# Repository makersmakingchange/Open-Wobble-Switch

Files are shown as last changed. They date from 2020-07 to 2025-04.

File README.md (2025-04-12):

# Open Wobble Switch

## Overview
The Open Wobble Switch is a cost effective, open source assistive switch similar to commercially available Wobble Switches. The switch is activated by applying force to and moving a wand in any direction. The switch can be activated by various body parts including the limbs and head. It provides a momentary closed contact that can be used to activate various assistive devices. The Open Wobble Switch has an interchangeable topper that can be swapped for different shapes and sizes. The switch requires approximately 0.55 N (55 gf) and about 24 mm of travel to operate, though this will vary a bit depending on the topper attached. 

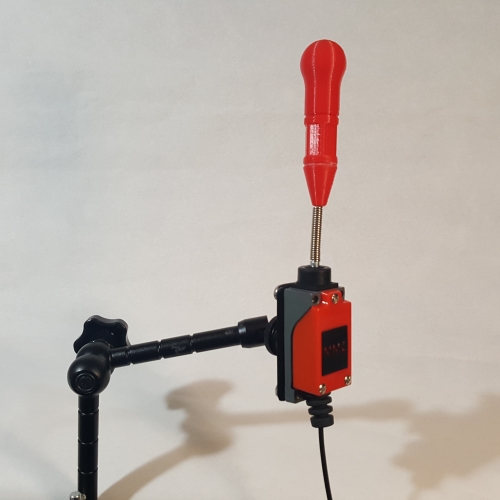
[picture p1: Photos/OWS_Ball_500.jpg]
Open Wobble Switch


Last Updated: 2024-Mar-21

## More info at
- [Makers Making Change Device Page](https://www.makersmakingchange.com/project/open-wobble-switch/)

## Getting Started

### 1. Order the Off-The-Shelf Components

The [Bill of Materials](/Documentation/Open_Wobble_Switch_BOM.xlsx) lists all of the parts and components required to build the Open Wobble Switch. The main switch component needs to be ordered online. The rest of the off-the-shelf components are also online or may be available in smaller quantities at your local hardware store or dollar store.

### 2. Print the 3D Printable components

Print the components for the switch and one or more toppers.

All of the files and individual print files can be in the [/Build_Files/3D_Printing_Files](/Build_Files/3D_Printing/) folder.

### 3. Assemble the Switch and Toppers

Reference the [assembly instructions](/Documentation/Open_Wobble_Switch_Instructions.pdf) for the tools and steps required to build each portion.

## Files
### Documentation
| Document             | Version | Link |
|----------------------|---------|------|
| Design Rationale     | 1.1     | [Open_Wobble_Switch_Design_Rationale](/Documentation/Open_Wobble_Switch_Design_Rationale.pdf)     |
| Bill of Materials    | 1.1     | [Open_Wobble_Switch_BOM](/Documentation/Open_Wobble_Switch_BOM.csv)     |
| Assembly Guide       | 1.1     | [Open_Wobble_Switch_Instructions](/Documentation/Open_Wobble_Switch_Instructions.pdf)     |
| Maker Checklist      | 1.1     | [Open_Wobble_Switch_Checklist](/Documentation/Open_Wobble_Switch_Checklist.pdf)     |
| Quick Guide          | 1.1     | [Open_Wobble_Switch_Quick_Guide](/Documentation/Open_Wobble_Switch_Quick_Guide.pdf)    |
| Changelog            | 1.1     | [Open_Wobble_Switch_Changelog](/Documentation/Open_Wobble_Switch_Changelog.pdf)     |

### Design Files
[CAD Files](/Design_Files)

### Build Files
 - [3D Printing Files](/Build_Files/3D_Printing)
 - [V1.1 3MF](/Build_Files/3D_Printing/OWS_All_v1.1.3mf)

## Attribution
Designers:
 - Birk Zukowsky
 - Gabriel Chu
 - Jake McIvor

## License
<br /><span xmlns:dct="http://purl.org/dc/terms/" property="dct:title">Open Wobble Switch</span> by <a xmlns:cc="http://creativecommons.org/ns#" href="www.makersmakingchange.com" property="cc:attributionName" rel="cc:attributionURL">Neil Squire</a> is licensed under a <a rel="license" href="http://creativecommons.org/licenses/by-sa/4.0/">Creative Commons Attribution-ShareAlike 4.0 International License</a>.

---
<!-- ABOUT MMC START -->
## About Makers Making Change
[Makers Making Change Logo](https://www.makersmakingchange.com/)

Makers Making Change is a program of [Neil Squire](https://www.neilsquire.ca/), a Canadian non-profit that uses technology, knowledge, and passion to empower people with disabilities.

Makers Making Change leverages the capacity of community based Makers, Disability Professionals and Volunteers to develop and deliver affordable Open Source Assistive Technologies.

 - Website: [www.MakersMakingChange.com](https://www.makersmakingchange.com/)
 - GitHub: [makersmakingchange](https://github.com/makersmakingchange)
 - Bluesky: [@makersmakingchange.bsky.social](https://bsky.app/profile/makersmakingchange.bsky.social)
 - Instagram: [@makersmakingchange](https://www.instagram.com/makersmakingchange)
 - Facebook: [makersmakechange](https://www.facebook.com/makersmakechange)
 - LinkedIn: [Neil Squire Society](https://www.linkedin.com/company/neil-squire-society/)
 - Thingiverse: [makersmakingchange](https://www.thingiverse.com/makersmakingchange/about)
 - Printables: [MakersMakingChange](https://www.printables.com/@MakersMakingChange)

### Contact Us
For technical questions, to get involved, or to share your experience we encourage you to [visit our website](https://www.makersmakingchange.com/) or [contact us](https://www.makersmakingchange.com/s/contact).
<!-- ABOUT MMC END -->

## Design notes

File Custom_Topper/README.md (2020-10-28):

# Custom Toppers for the Open Wobble Switch

One of the unique features of the Open Wobble Switch is the ability to swap the toppers and create custom toppers. To make the process of creating a custom topper as easy as possible, we've included some additional files and instructions.

The switch has an M12-1.75 x 7mm length external thread to interface with the topper.

## OpenSCAD
https://dkprojects.net/openscad-threads/

## TinkerCAD
https://www.tinkercad.com/things/hLjlR0M9PSN-openwobbletopper-flat

## Fusion 360

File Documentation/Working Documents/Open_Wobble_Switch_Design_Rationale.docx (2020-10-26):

# Introduction

A wobble switch is an assistive switch that can be activated by moving a wand topper. Wobble switches are useful for a variety of users, but can be especially useful for those with poor gross motor control. These switches can be mounted easily and activated by pushing the wand in any direction. The switches can be operated with very little force. The switches can be activated with various parts of the body including: hands, head, chin, tongue through cheek.

Activating the wobble switch completes the circuit and activates the other end. When the 3.5 mm plug is inserted into an input, it activates the device it is plugged into. The switch can be plugged into different devices such as the Xbox Adaptive Controller to act as an extension of a button. This enables the user to activate a multitude of devices (or device buttons) without the use of fine motor control.

Commercial Options

Table 1 Commercially Available Wobble Switches

Name | Vendor | Cost | Link
Ultimate Assistive Technology Switch | Enabling Devices | $80 USD Switch, $150 USD w/ mount | https://enablingdevices.com/product/ultimate-switch/
Wobble Switch | Prentrom | $195 | https://store.prentrom.com/wobble-switch
Wobble Switch | AbleNet | $100 USD | https://www.ablenetinc.com/wobble-switch
Wobble Switch | AMDi | $100 USD | https://www.amdi.net/products/switches/wobble-switch/

# Switch Selection

The existing commercial switches appeared to be a modified commercial product, so this provided a starting point for the design. A similar looking industrial switch was found and tested and provided similar functionality.

## Mini Limit Switch

The switch selected for the base of the Wobble Switch is a ME-8169, which is available from a number of different manufacturers. This limit switch is typically used for CNC machines and there are a few different variants for the activation end. The end most suitable for a Wobble switch is the ‘Flexible Spring Arm’.

An alternative design may be the ME-9101. This variant is typically listed as a ‘flexible spring arm limit switch’. Instead of the wire, it features a longer coil. (https://www.amazon.ca/Uxcell-Me-9101-Momentary-Adjustable-Flexible/dp/B00UBWK8X6)

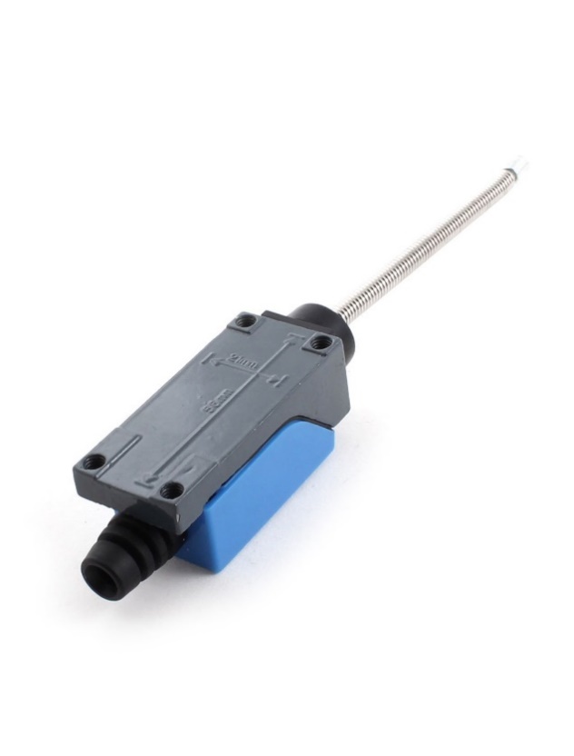
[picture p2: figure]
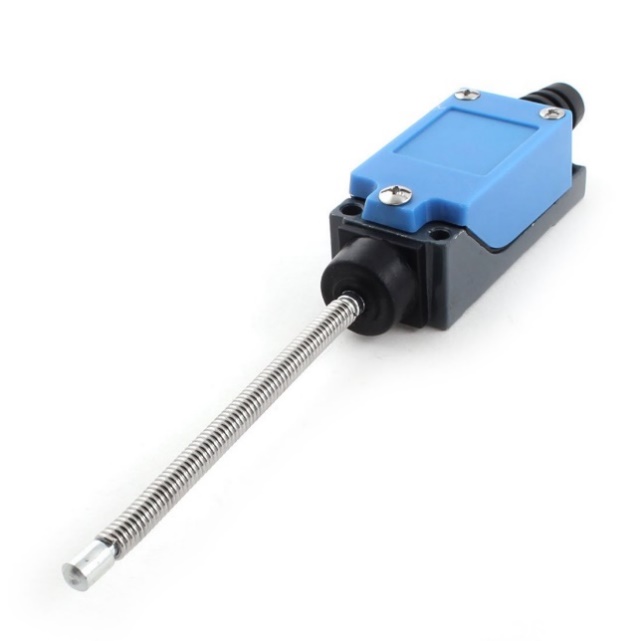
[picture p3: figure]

# Mounting

To keep the switch versatile, it must be easy to mount in a variety of positions and easy to fine-tune the adjustment. Like many of the open source assistive technology, we chose to include a female ½-20 UNC thread so that the switch could be mounted using camera and tripod accessories as well as most other standard assistive technology mounting solutions.

The limit switch has four threaded holes in the metal base spaced on a rectangle 21 mm x 56 mm. This bolt pattern appears to be consistent between manufacturers and different limit switch styles.

The mounting adapter was designed to utilize a ¼-20 UNC, 5/16" tee nut and the four existing mounting holes in the switch. It attaches using 4 M5x0.8 by 10 mm long machine screws. Pan head machine screws, ideally with a Phillips drive, were selected to provide a low profile and so a common screwdriver could be used instead of a hex key.

## Mounting options

- Gooseneck
- Articulating arm / Magic arm (e.g. https://www.amazon.ca/SmallRig-Adjustable-Articulating-Monitor-Lights-2066/dp/B076KDDBW5, $20)
- Loc-Line

# Wand Topper

The bare wire of the limit switch has a pointy end and is not safe to be used on its own. Commercial wobble switches tend to have a ball or rounded cylinder that cover the activation portion.

The initial design for the wire topper was a 4 part design, but this was too challenging to assemble.

Feedback was received on the initial proof of concept prototype that a Tee-shaped topper / handle would be useful.

A versatile feature of the wobble switch is its adaptable toppers. An anchored hex-grip base with extended threads allows for the customizability of different toppers. The T-Topper consists of five separate pieces: the socket, the top and bottom halves of the T, and two pins to hold the halves in the correct position when assembling. The socket was created to allow the female threads to be printed upwards (yielding more accurate 3D printed threads), while enabling the two T halves to be printed on the flat surface to avoid the use of support material. The same theory applies to the Ball-Topper, which only uses one pin. Printing the file vertically is the most logical orientation for the Hand-Topper, which is why the socket is combined into one file and printed as one piece.

Other attachment methods were ideated for attaching both the wand to the wire as well as between the base and the topper. Different methods were sketched, and some were prototyped such as dove tails and varying threads. Super glue was discovered to be the best option in connecting the base to the wire as the burr on the end on most units’ wire, along with inconsistent 3D printer tuning and accuracy, could not be proven to work consistently without high dexterity.

There is potential for future topper designs to be created. Depending on what is requested by an Occupational Therapist or user of the wobble switch, different toppers can be built to suit their needs, for either functionality, aesthetics, or personal interests. Figure 3 shows a variety of possible topper options.

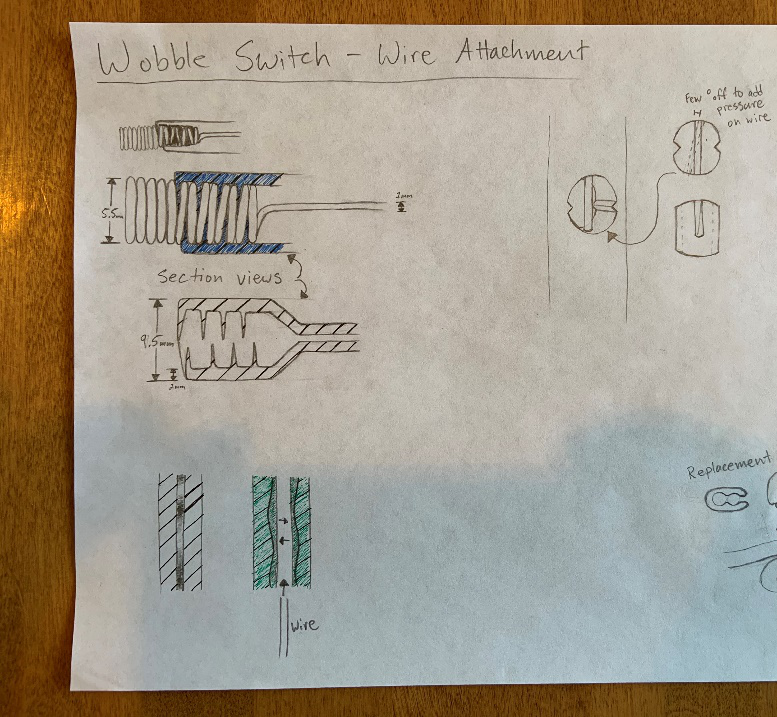
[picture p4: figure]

Figure 1: Wire Attachment Ideation

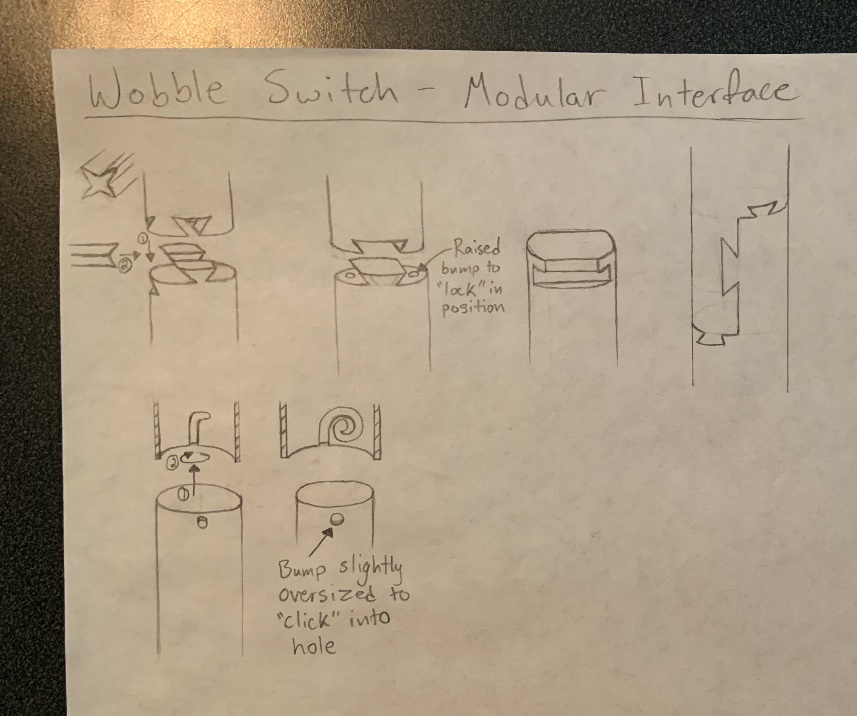
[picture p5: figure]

Figure 2: Modular Interface Ideation

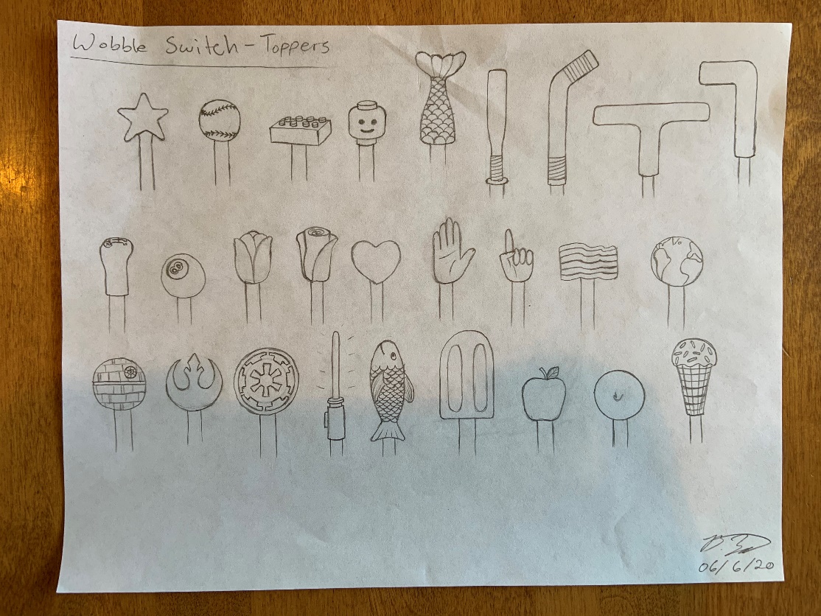
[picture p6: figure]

Figure 3: Wobble Switch Topper Ideation

# Testing

A preliminary proof of concept was tested with several users in an adaptive gaming setup. The wobble switch was mounted to an articulated arm and positioned near the face to provide an additional input to the Xbox Adaptive Controller.

# Version 1.1 Changes

This section will cover the changes and updates that was discussed in the previous section. The design changes focus more on improving the earlier design.

# Toppers

The original toppers were designed with a topper socket in the design which resulted in the need to print the topper pieces in half to properly mount and assemble. Example below.

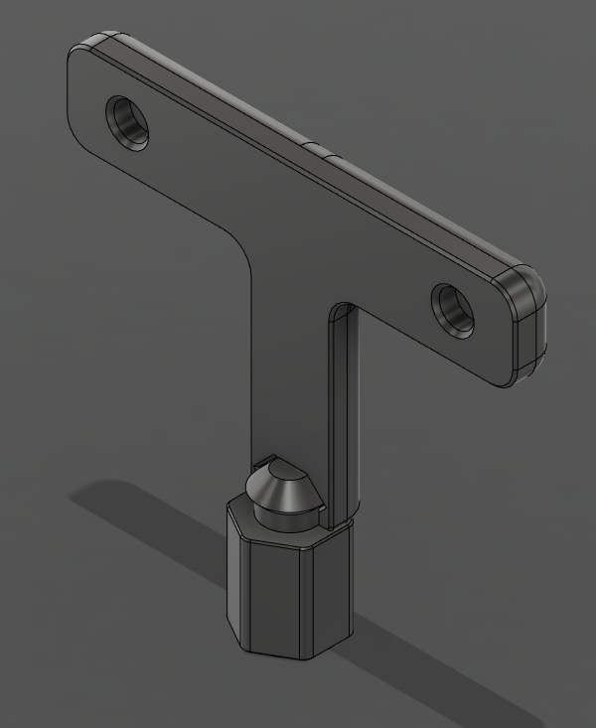
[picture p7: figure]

This made the assembly a little bit more complicated and required the use of glue between the two halves of the topper which, depending on the user, may not have enough glue to secure the two halves together. One idea to solve this process was to integrate a thread into the base of the topper and to print the topper as one piece. Shown below.

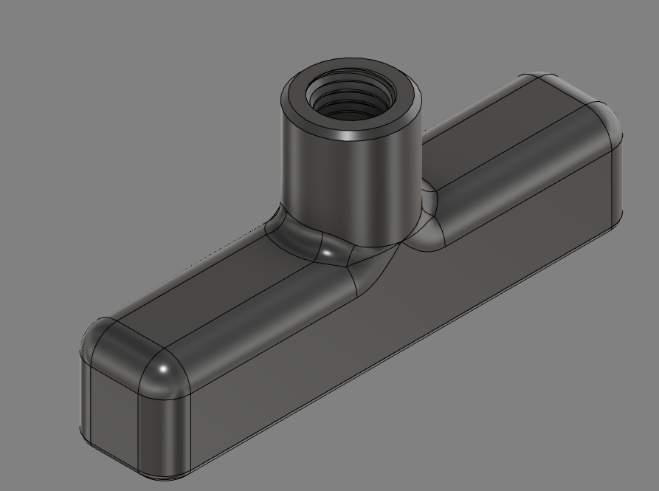
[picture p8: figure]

With the integrated thread we can make the topper piece shorter as well as take away the topper socket piece. This solves another issue with the original design where the weight of the topper assembly causes the switch to bend and possibly activate due to the weight of the assembly. The same concept is used for the other toppers that were designed for example, a rounded ball topper. The topper socket in the original design allows the topper piece to rotate which is undesirable but will be discussed in the next section.

# Topper Socket

The topper socket that was originally designed allows for the assembly and mounting of the topper pieces. However, with the switch having the ability to rotate, the topper socket’s original design with its own ability to rotate the top piece is no desired. Therefore, the topper socket was changed from a circular socket to a squarer or hexagonal shape to limit the amount of rotation of the topper piece. The main function of the topper socket is to allow custom pieces designed by users to be mounted onto the wobble switch.

# Male Threaded Piece

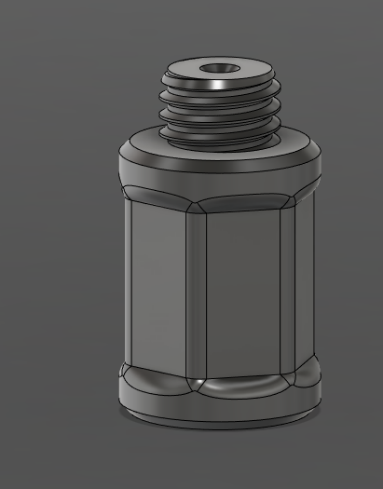
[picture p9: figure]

The male threaded piece shown above is the main mounting piece of the wobble switch assembly. One issue that arose when threading on the topper socket and this piece is that the hexagonal shapes may not match up and would have a sharp corner when the two pieces are threaded together. So, the top was rounded to take away the shape edge and any misalignment issues. This rounding is also done to the bottom of the piece so that it can also transition to the bottom piece.

# Bottom Transition Piece

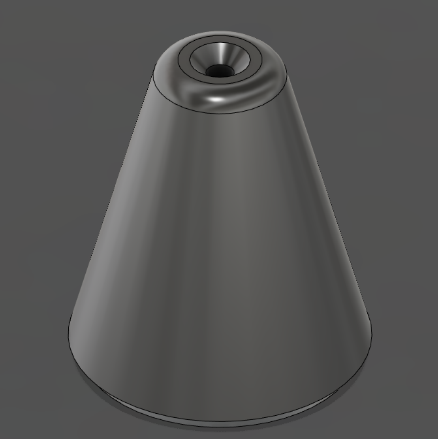
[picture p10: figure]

This transition piece is based off of the original Gluing jig and is mainly used as both a smoothing transition piece as well as the gluing jig for the entire assembly. This smoothens the transition between the wire and the handle pieces.

© 2020 by Neil Squire. “Open Wobble Switch Design Rationale” is licensed under the CC BY SA 4.0 License: http://creativecommons.org/licenses/by-sa/4.0 PAGE 1 OF 3 Design files available at https://www.makersmakingchange.com/project/open-wobble-switch/

V1.1 | OCTOBER 2020 Open Wobble Switch design rationale

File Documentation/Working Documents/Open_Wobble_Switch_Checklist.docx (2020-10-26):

To-do

- Determine which topper(s) the user wants
- Acquire off-the-shelf components
- Print 3D printable components
- Assemble the switch
- Test the switch
- Clean and disinfect the switch
- Package the switch in a sealed bag
- Print the Quick Guide

Items to Deliver to User

- Assembled, Tested, and cleaned Switch
- Quick Guide

© 2020 by Neil Squire. “Open Wobble Switch Maker Checklist” is licensed under the CC BY SA 4.0 License: http://creativecommons.org/licenses/by-sa/4.0 PAGE 1 OF 3 Design files available at https://www.makersmakingchange.com/project/open-wobble-switch/

V1.1 | OCTOBER 2020 Open Wobble Switch MAKER CHECKLIST

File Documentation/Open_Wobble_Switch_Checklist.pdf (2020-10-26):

V1.1 | OCTOBER 2020

# Open Wobble Switch

MAKER CHECKLIST

© 2020 by Neil Squire. (https://neilsquire.ca/) “Open Wobble Switch Maker Checklist” is licensed under the CC BY SA 4.0 License: http://creativecommons.org/licenses/bysa/4.0 (http://creativecommons.org/licenses/by-sa/4.0)
Design files available at https://www.makersmakingchange.com/project/open-wobble-switch/ | PAGE 1 OF 1

To-do

ð Determine which topper(s) the user wants
ð Acquire off-the-shelf components ð Print 3D printable components
ð Assemble the switch
ð Test the switch
ð Clean and disinfect the switch
ð Package the switch in a sealed bag ð Print the Quick Guide

Items to Deliver to User

ð Assembled, Tested, and cleaned Switch
ð Quick Guide

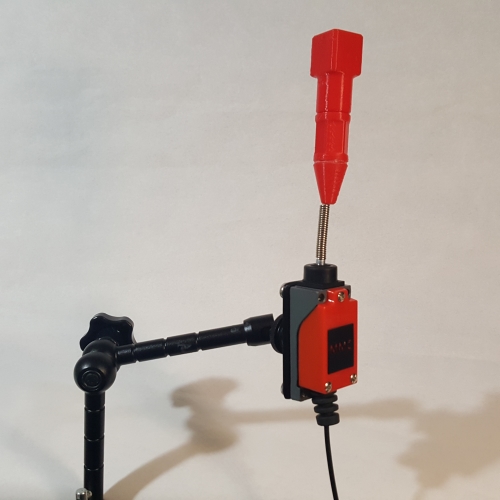
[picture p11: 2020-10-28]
Photos/OWS_Cube_500.jpg

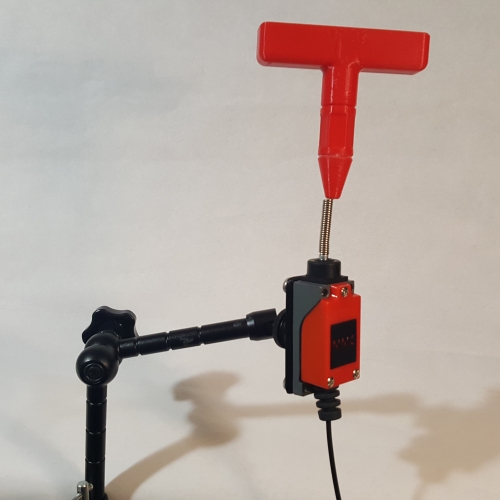
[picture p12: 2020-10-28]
Photos/OWS_Tee_500.jpg

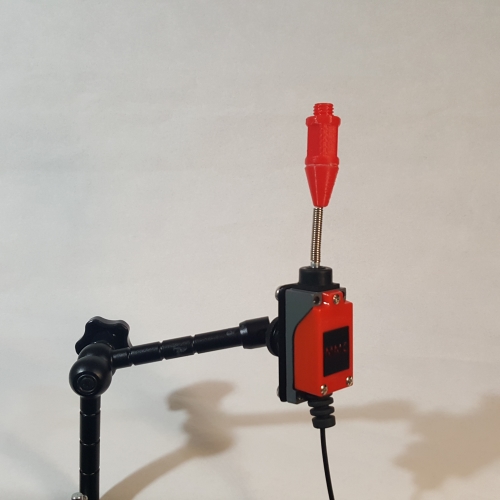
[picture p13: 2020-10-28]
Photos/OWS_Topper_Connector_500.jpg

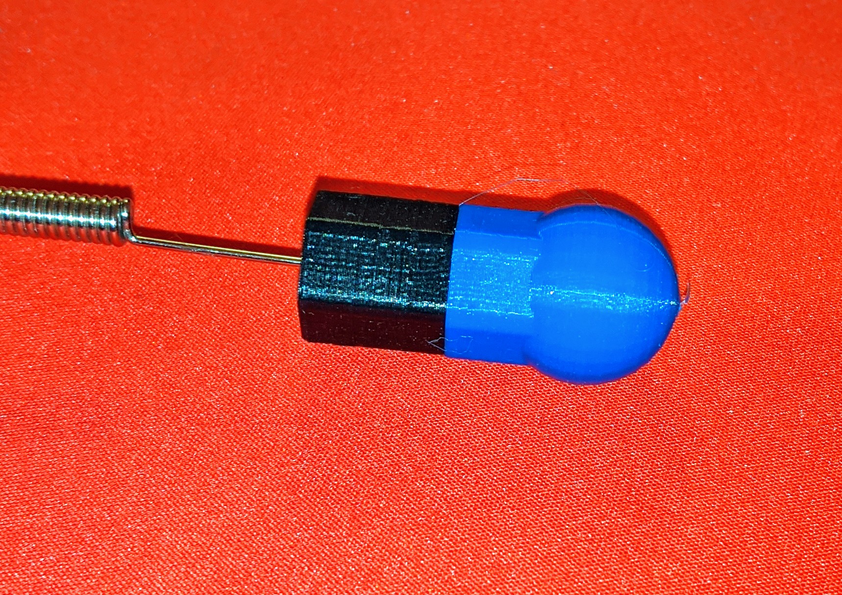
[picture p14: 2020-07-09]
Custom_Topper/OpenSCAD/OpenSCAD_Topper.jpg

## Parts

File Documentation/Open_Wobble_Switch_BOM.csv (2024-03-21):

PBS | Qty | Component | Component name | Line Item | Supplier | Manufacturer | MPN | SKU | Pkg Qty | Pkg Cost | PkG Reqd | MinCost | Unit Cost | Extended |  | URL (Canada)
OWS-000-000 |  |  | Open Wobble Switch |  |  |  |  |  |  |  |  | $82.33 |  |  | $15.06
OWS-100-000 | 1 | Required | Switch Assembly |  |  |  |  |  |  |  |  |  |  |  | $14.61
OWS-100-001 | 1 | Required | Limit Switch, Momentary Flexible Coil Spring |  | Amazon | Uxcell | a18091500ux0012 | B07KM22TZ2 | 3 | $14.14 | 1 | $14.14 | $4.71 | $4.71 |  | https://www.amazon.ca/uxcell%C2%AE-ME-8166-Flexible-Spring-Momentary/dp/B07KM22TZ2
OWS-110-002 | 1 | Required | Cable, 3.5 mm Mono, 6 ft length |  | Amazon | TNP Products | CBL_35N_MM_15FT | B01MCR16CZ | 2 | $12.99 | 1 | $12.99 | $6.50 | $6.50 |  | https://www.amazon.ca/TNP-3-5mm-Mono-Cable-15FT/dp/B01MCR16CZ
OWS-660-001 | 1 | Required | Tee Nut, ¼-20 UNC, 5/16" length |  | Amazon | Bolt Dropper |  | B01MSVU3WF | 100 | $15.92 | 1 | $15.92 | $0.16 | $0.16 |  | https://www.amazon.ca/Bolt-Dropper-Pronged-Climbing-Cabinetry/dp/B01MSVU3WF
OWS-640-002 | 4 | Required | Screw, Pan Head, M5x0.8, 10 mm length |  | Amazon |  |  |  | 10 | $7.55 | 1 | $7.55 | $0.76 | $3.02 |  | https://www.amazon.ca/Prime-Line-9131356-Machine-Phillips-Stainless/dp/B07D5S35GJ
OWS-640-003 | 1 | Optional | Hex Bolt, 1/4-20 UNC, 3/4" Length |  | Amazon | Bolt Dropper | ZF-VMHQ-E6IF | B075DJHTNG | 100 | $22.30 | 1 | $22.30 | $0.22 | $0.22 |  | https://www.amazon.ca/Stainless-Steel-100pcs-Bolt-Dropper/dp/B075DJHTNG
OWS-110-003 | 1 | Required | Zip Tie |  | Amazon |  |  |  | 100 | $8.99 | 1 | $8.99 | $0.09 | $0.09 |  | https://www.amazon.ca/TR-Industrial-TR88301-Multi-Purpose-Cable/dp/B01018DB2E
OWS-111-001 | 1 | Required | Mounting Adapter (3D Printed) |  |  |  |  |  | 1 | $0.20 | 1 | $0.20 | $0.20 | $0.20 |  | https://github.com/makersmakingchange/Open-Wobble-Switch/blob/master/Build_Files/3D_Printing/OWS_Mounting_Adapter.stl
OWS-110-005 | 1 | Optional | Nameplate (3D Printed) |  |  |  |  |  | 1 | $0.01 | 1 | $0.01 | $0.01 | $0.01 |  | https://github.com/makersmakingchange/Open-Wobble-Switch/blob/master/Build_Files/3D_Printing/OWS_Nameplate.stl
OWS-110-006 | 1 | Required | Topper Connector (3D Printed) |  |  |  |  |  | 1 | $0.07 | 1 | $0.07 | $0.07 | $0.07 |  | https://github.com/makersmakingchange/Open-Wobble-Switch/blob/master/Build_Files/3D_Printing/OWS_Topper_Connector.stl
OWS-110-007 | 1 | Required | Topper Transition (3D Printed) |  |  |  |  |  | 1 |  | 1 |  |  |  |  | https://github.com/makersmakingchange/Open-Wobble-Switch/blob/master/Build_Files/3D_Printing/OWS_Topper_Transition.stl
OWS-210-000 | 1 | Required | Ball Topper Assembly |  |  |  |  |  |  |  |  |  |  |  | 0.08
OWS-200-001 | 1 | Required | Topper Ball (3D Printed) |  |  |  |  |  | 1 | $0.08 | 1 | $0.08 | $0.08 | $0.08 |  | https://github.com/makersmakingchange/Open-Wobble-Switch/blob/master/Build_Files/3D_Printing/OWS_Topper_Ball.stl
OWS-220-000 | 1 | Optional | Tee Topper Assembly |  |  |  |  |  |  |  |  |  |  |  | 0.08
OWS-200-001 | 1 | Optional | Topper Tee (3D Printed) |  |  |  |  |  | 1 | $0.08 | 1 | $0.08 | $0.08 | $0.08 |  | https://github.com/makersmakingchange/Open-Wobble-Switch/blob/master/Build_Files/3D_Printing/OWS_Topper_Tee.stl
OWS-240-000 | 1 | Optional | Custom Topper Assembly |  |  |  |  |  |  |  |  |  |  |  | 0.08
OWS-240-001 | 1 | Optonal | Custom Topper Base (3D Printed) |  |  |  |  |  | 1 | $0.08 | 1 | $0.08 | $0.08 | $0.08 |  | https://github.com/makersmakingchange/Open-Wobble-Switch/blob/master/Build_Files/3D_Printing/OWS_Topper_Tee.stl
OWS-100-001 | 0 | Alternate | Limit Switch, Momentary Flexible Coil Spring |  | Amazon |  |  |  | 2 | $14.93 | 0 | $- | $7.47 | $- |  | https://www.amazon.ca/Xenocam-ME-8169-Whisker-Flexible-Momentary/dp/B07SHMQTQN
OWS-100-001 | 0 | Alternate | Limit Switch, Momentary Flexible Coil Spring |  | Amazon |  |  |  | 3 | $19.73 | 0 | $- | $6.58 | $- |  | https://www.amazon.ca/uxcell%C2%AE-ME-8166-Flexible-Spring-Momentary/dp/B07KM22TZ2
OWS-100-001 | 0 | Alternate | Limit Switch, Momentary Flexible Coil Spring |  | Amazon |  |  |  | 1 | $14.19 | 0 | $- | $14.19 | $- |  | https://www.amazon.ca/Uxcell-ME-8169-Flexible-Spring-Switch/dp/B00D83C54U
OWS-640-003 | 0 | Alternate | Hex Bolt, 1/4-20 UNC, 3/4" Length |  | Home Depot |  |  |  | 1 | $0.24 | 0 | $- | $0.24 | $- |  | https://www.homedepot.ca/product/paulin-1-4-inch-x-3-4-inch-hex-head-cap-screw-zinc-plated-grade-5-unc/1000132018
OWS-660-001 | 0 | Alternate | Tee Nut, ¼-20 UNC, 5/16" length |  | Home Depot |  |  |  | 1 | $0.48 | 0 | $- | $0.48 | $- |  | https://www.homedepot.ca/product/paulin-1-4-inch-20-tee-nuts-4-prong-5-16-inch-barrel-length/1000129429

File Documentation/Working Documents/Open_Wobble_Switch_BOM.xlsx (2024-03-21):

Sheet: OWS_BOM_Canada
PBS | Qty | Component | Component name | Supplier | Manufacturer | MPN | SKU | Pkg Qty | Pkg Cost | PkG Reqd | MinCost | Unit Cost | Extended |  | URL (Canada)
OWS-000-000 |  |  | Open Wobble Switch |  |  |  |  |  |  |  | $82.33 |  |  | $15.06
OWS-100-000 | 1 | Required | Switch Assembly |  |  |  |  |  |  |  |  |  |  | $14.61
OWS-100-001 | 1 | Required | Limit Switch, Momentary Flexible Coil Spring | Amazon | Uxcell | a18091500ux0012 | B07KM22TZ2 | 3 | $14.14 | 1 | $14.14 | $4.71 | $4.71 |  | https://www.amazon.ca/uxcell%C2%AE-ME-8166-Flexible-Spring-Momentary/dp/B07KM22TZ2
OWS-110-002 | 1 | Required | Cable, 3.5 mm Mono, 6 ft length | Amazon | TNP Products | CBL_35N_MM_15FT | B01MCR16CZ | 2 | $12.99 | 1 | $12.99 | $6.50 | $6.50 |  | https://www.amazon.ca/TNP-3-5mm-Mono-Cable-15FT/dp/B01MCR16CZ
OWS-660-001 | 1 | Required | Tee Nut, ¼-20 UNC, 5/16" length | Amazon | Bolt Dropper |  | B01MSVU3WF | 100 | $15.92 | 1 | $15.92 | $0.16 | $0.16 |  | https://www.amazon.ca/Bolt-Dropper-Pronged-Climbing-Cabinetry/dp/B01MSVU3WF
OWS-640-002 | 4 | Required | Screw, Pan Head, M5x0.8, 10 mm length | Amazon |  |  |  | 10 | $7.55 | 1 | $7.55 | $0.76 | $3.02 |  | https://www.amazon.ca/Prime-Line-9131356-Machine-Phillips-Stainless/dp/B07D5S35GJ
OWS-640-003 | 1 | Optional | Hex Bolt, 1/4-20 UNC, 3/4" Length | Amazon | Bolt Dropper | ZF-VMHQ-E6IF | B075DJHTNG | 100 | $22.30 | 1 | $22.30 | $0.22 | $0.22 |  | https://www.amazon.ca/Stainless-Steel-100pcs-Bolt-Dropper/dp/B075DJHTNG
OWS-110-003 | 1 | Required | Zip Tie | Amazon |  |  |  | 100 | $8.99 | 1 | $8.99 | $0.09 | $0.09 |  | https://www.amazon.ca/TR-Industrial-TR88301-Multi-Purpose-Cable/dp/B01018DB2E
OWS-111-001 | 1 | Required | Mounting Adapter (3D Printed) |  |  |  |  | 1 | $0.20 | 1 | $0.20 | $0.20 | $0.20 |  | https://github.com/makersmakingchange/Open-Wobble-Switch/blob/master/Build_Files/3D_Printing/OWS_Mounting_Adapter.stl
OWS-110-005 | 1 | Optional | Nameplate (3D Printed) |  |  |  |  | 1 | $0.01 | 1 | $0.01 | $0.01 | $0.01 |  | https://github.com/makersmakingchange/Open-Wobble-Switch/blob/master/Build_Files/3D_Printing/OWS_Nameplate.stl
OWS-110-006 | 1 | Required | Topper Connector (3D Printed) |  |  |  |  | 1 | $0.07 | 1 | $0.07 | $0.07 | $0.07 |  | https://github.com/makersmakingchange/Open-Wobble-Switch/blob/master/Build_Files/3D_Printing/OWS_Topper_Connector.stl
OWS-110-007 | 1 | Required | Topper Transition (3D Printed) |  |  |  |  | 1 |  | 1 |  |  |  |  | https://github.com/makersmakingchange/Open-Wobble-Switch/blob/master/Build_Files/3D_Printing/OWS_Topper_Transition.stl
OWS-210-000 | 1 | Required | Ball Topper Assembly |  |  |  |  |  |  |  |  |  |  | 0.08
OWS-200-001 | 1 | Required | Topper Ball (3D Printed) |  |  |  |  | 1 | $0.08 | 1 | $0.08 | $0.08 | $0.08 |  | https://github.com/makersmakingchange/Open-Wobble-Switch/blob/master/Build_Files/3D_Printing/OWS_Topper_Ball.stl
OWS-220-000 | 1 | Optional | Tee Topper Assembly |  |  |  |  |  |  |  |  |  |  | 0.08
OWS-200-001 | 1 | Optional | Topper Tee (3D Printed) |  |  |  |  | 1 | $0.08 | 1 | $0.08 | $0.08 | $0.08 |  | https://github.com/makersmakingchange/Open-Wobble-Switch/blob/master/Build_Files/3D_Printing/OWS_Topper_Tee.stl
OWS-240-000 | 1 | Optional | Custom Topper Assembly |  |  |  |  |  |  |  |  |  |  | 0.08
OWS-240-001 | 1 | Optonal | Custom Topper Base (3D Printed) |  |  |  |  | 1 | $0.08 | 1 | $0.08 | $0.08 | $0.08 |  | https://github.com/makersmakingchange/Open-Wobble-Switch/blob/master/Build_Files/3D_Printing/OWS_Topper_Tee.stl
OWS-100-001 | 0 | Alternate | Limit Switch, Momentary Flexible Coil Spring | Amazon |  |  |  | 2 | $14.93 | 0 | $0.00 | $7.46 | $0.00 |  | https://www.amazon.ca/Xenocam-ME-8169-Whisker-Flexible-Momentary/dp/B07SHMQTQN
OWS-100-001 | 0 | Alternate | Limit Switch, Momentary Flexible Coil Spring | Amazon |  |  |  | 3 | $19.73 | 0 | $0.00 | $6.58 | $0.00 |  | https://www.amazon.ca/uxcell%C2%AE-ME-8166-Flexible-Spring-Momentary/dp/B07KM22TZ2
OWS-100-001 | 0 | Alternate | Limit Switch, Momentary Flexible Coil Spring | Amazon |  |  |  | 1 | $14.19 | 0 | $0.00 | $14.19 | $0.00 |  | https://www.amazon.ca/Uxcell-ME-8169-Flexible-Spring-Switch/dp/B00D83C54U
OWS-640-003 | 0 | Alternate | Hex Bolt, 1/4-20 UNC, 3/4" Length | Home Depot |  |  |  | 1 | $0.24 | 0 | $0.00 | $0.24 | $0.00 |  | https://www.homedepot.ca/product/paulin-1-4-inch-x-3-4-inch-hex-head-cap-screw-zinc-plated-grade-5-unc/1000132018
OWS-660-001 | 0 | Alternate | Tee Nut, ¼-20 UNC, 5/16" length | Home Depot |  |  |  | 1 | $0.48 | 0 | $0.00 | $0.48 | $0.00 |  | https://www.homedepot.ca/product/paulin-1-4-inch-20-tee-nuts-4-prong-5-16-inch-barrel-length/1000129429

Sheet: PBS
Open Wobble Switch - Product Breakdown Structure
PBS # | Name | Type | Build | QTY | Comment
OWS-000-000 | Open Wobble Switch | Assembly |  | 1
OWS-100-000 | Open Wobble Switch Assembly | Assembly |  | 1
OWS-110-000 | Switch Assembly | Assembly |  | 1
OWS-110-001 | Limit Switch, | Hardware | Off-the-shelf | 1
OWS-110-002 | Cable | Hardware | Off-the-shelf | 1
OWS-110-003 | Zip Ties | Hardware | Off-the-shelf | 1
OWS-111-000 | Mounting Plate Assembly | Assembly |  | 1
OWS-111-001 | Mounting Plate Adapter | Designed Part | 3D Print | 1
OWS-660-001 | Tee Insert Nut | Hardware | Off-the-shelf | 1
OWS-640-002 | Screw, Pan Head, M5x0.8, 10 mm length | Hardware | Off-the-shelf | 4
OWS-640-003 | Hex Bolt, 1/4-20 UNC, 3/4" Length | Hardware | Off-the-shelf | 1
OWS-110-005 | Name Plate | Designed Part | 3D Print | 1
OWS-110-006 | Topper Connector | Designed Part | 3D Print | 1
OWS-110-007 | Topper Transition | Designed Part | 3D Print | 1
OWS-200-000 | Topper Assemblies | Assembly |  | 1
OWS-210-000 | Ball Topper Assembly | Assembly |  | 1
OWS-200-001 | Topper Ball | Designed Part | 3D Print | 1
OWS-220-000 | Tee Topper Assembly | Assembly |  | 1
OWS-200-001 | Topper Tee | Designed Part | 3D Print | 1
OWS-230-000 | Hand Topper Assembly | Assembly |  | 1
OWS-230-001 | Hand Topper | Designed Part | 3D Print | 1

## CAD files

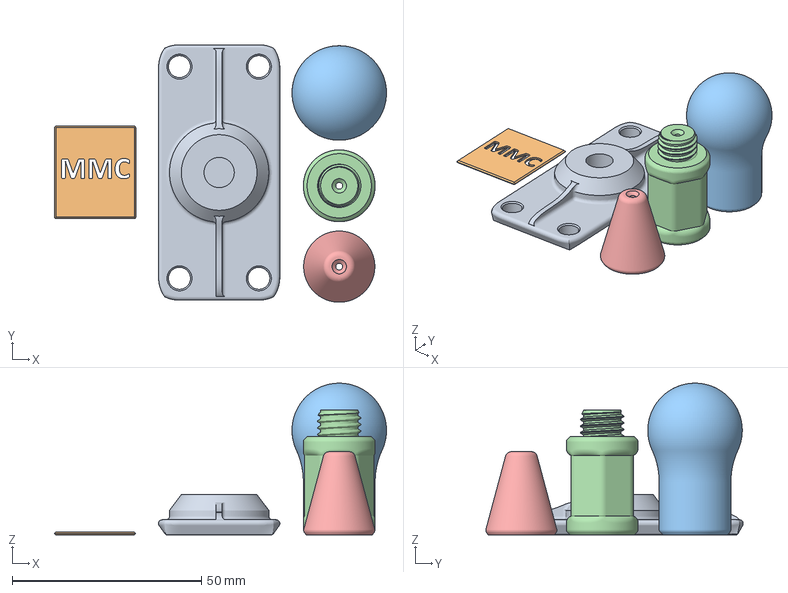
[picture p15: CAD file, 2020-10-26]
Build_Files/3D_Printing/OWS_All_v1.1.3mf
87.8 x 68.1 x 40.1 mm
OWS_Mounting_Adapter.stl
OWS_Nameplate.stl
OWS_Topper_Ball.stl
OWS_Topper_Connector.stl
OWS_Topper_Transition.stl

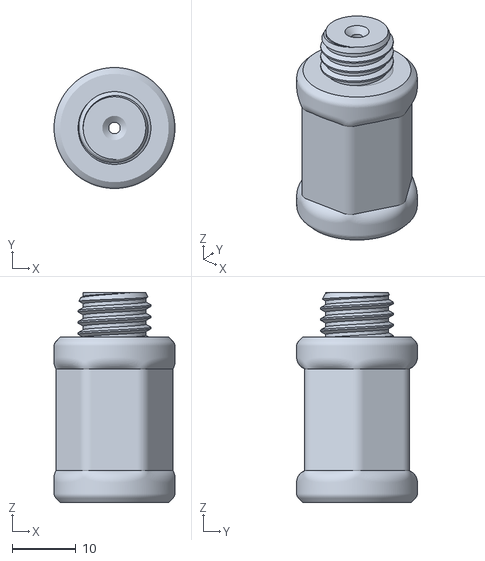
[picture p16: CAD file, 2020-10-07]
Build_Files/3D_Printing/V1.1/OWS_Topper_Connector.stl
19.0 x 19.0 x 33.0

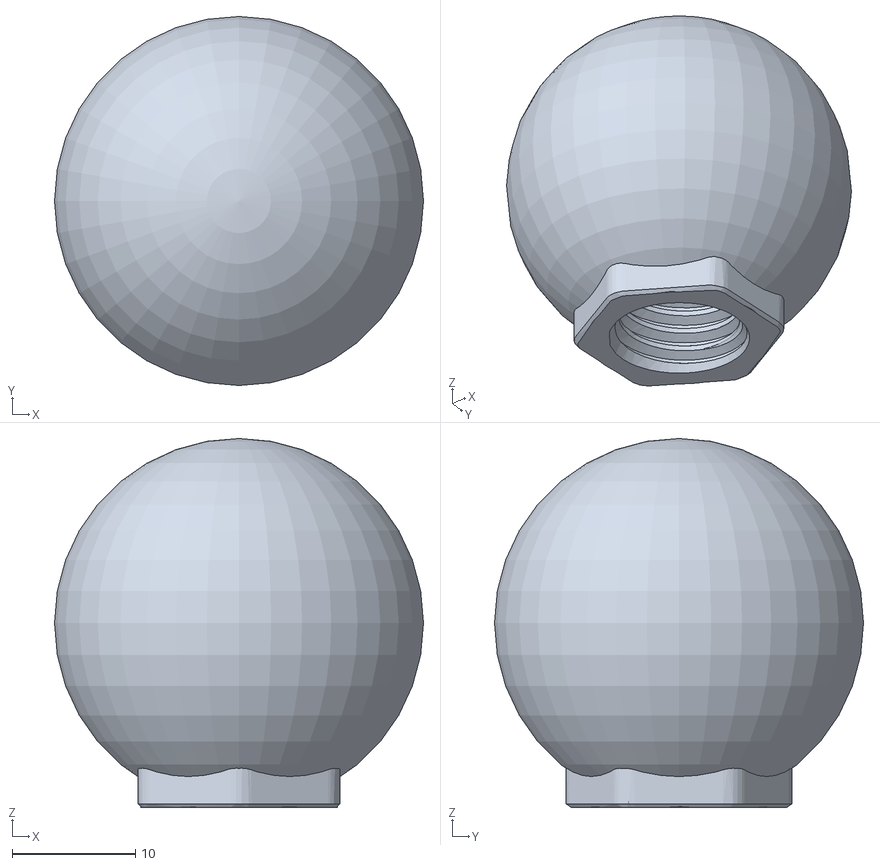
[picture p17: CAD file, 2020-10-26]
Custom_Topper/3D_Printing/Open_Wobble_Topper-ShortBall.stl
30.0 x 30.0 x 30.0

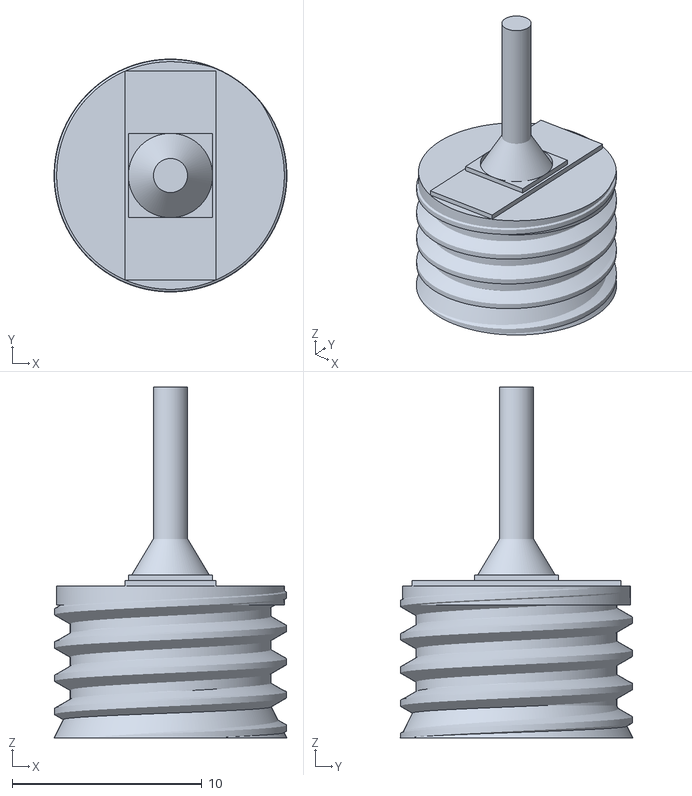
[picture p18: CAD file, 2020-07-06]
Custom_Topper/TinkerCAD/Wobble_Topper_Flat_Thread.stl
12.3 x 12.3 x 18.5

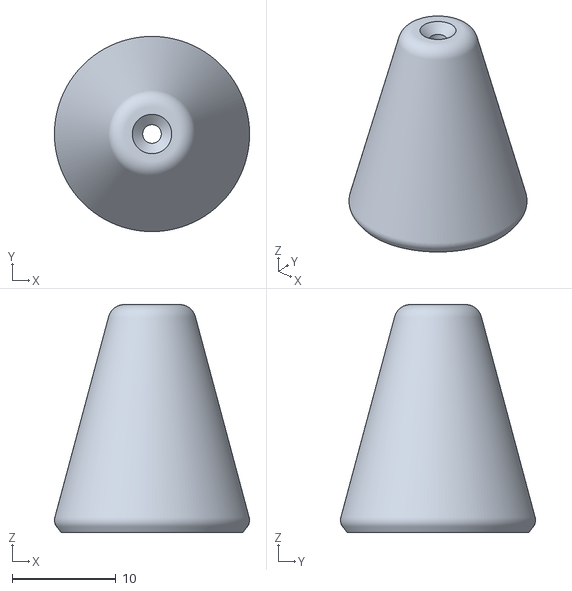
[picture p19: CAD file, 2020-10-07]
Build_Files/3D_Printing/V1.1/OWS_Topper_Transition.stl
18.8 x 18.8 x 22.0

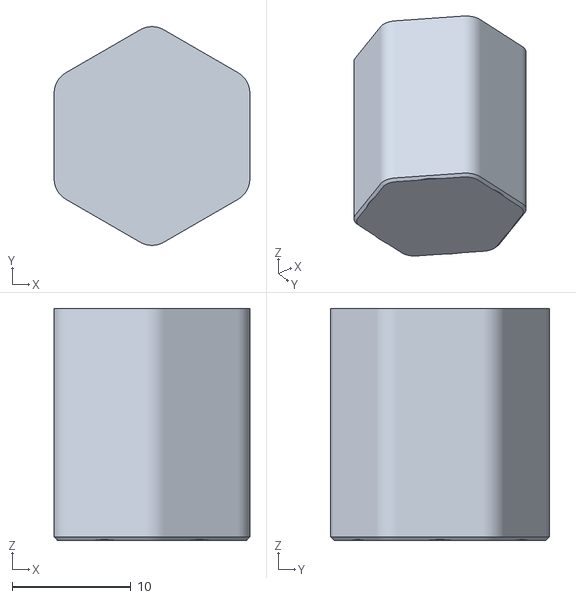
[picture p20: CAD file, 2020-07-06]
Custom_Topper/TinkerCAD/Wobble_Topper_Flat_Combined.stl
16.5 x 18.4 x 19.5

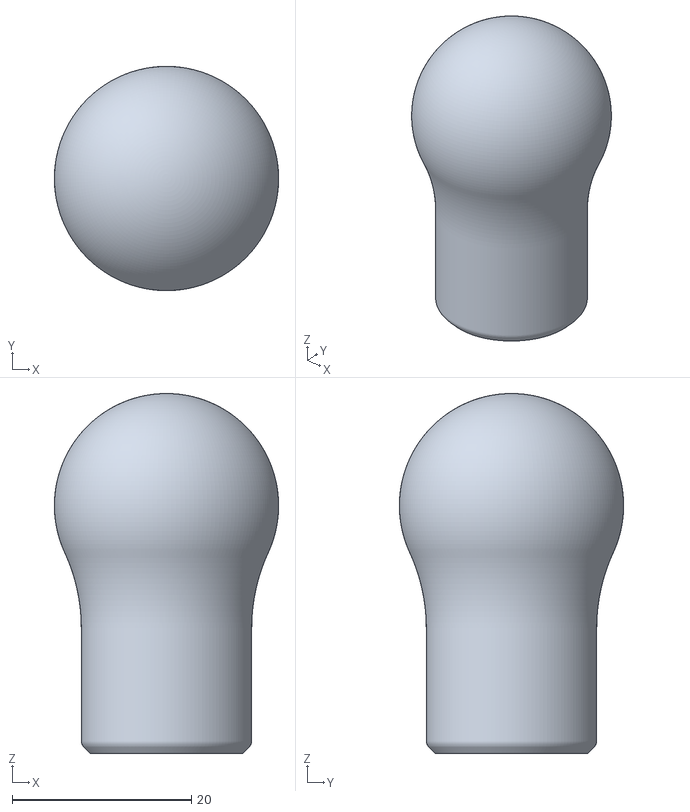
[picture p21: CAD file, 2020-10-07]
Build_Files/3D_Printing/V1.1/OWS_Topper_Ball.stl
25.0 x 25.0 x 40.1

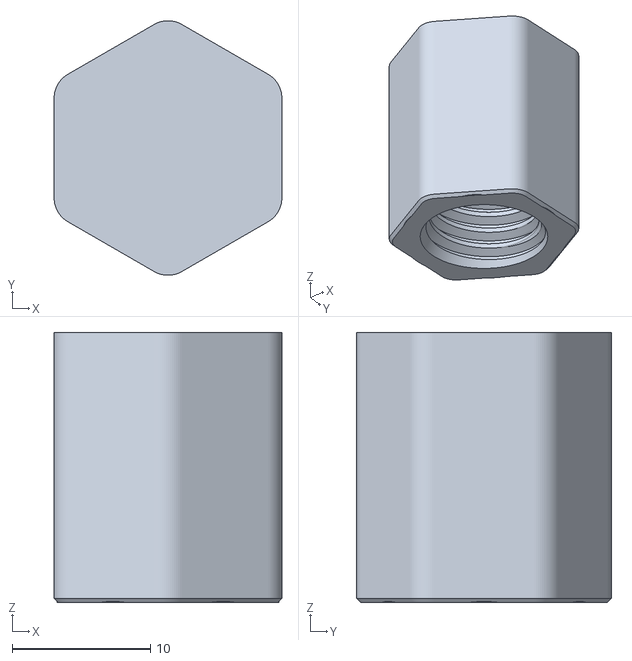
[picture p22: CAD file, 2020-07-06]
Custom_Topper/TinkerCAD/Wobble_Topper_Flat.stl
16.5 x 18.4 x 19.5

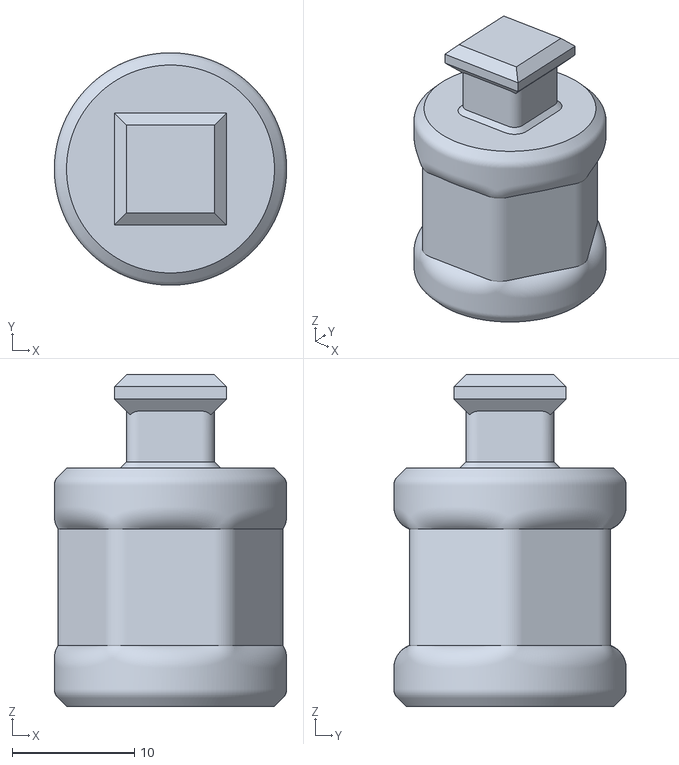
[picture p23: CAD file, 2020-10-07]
Build_Files/3D_Printing/V1.1/OWS_Topper_Peg.stl
19.0 x 19.0 x 27.1

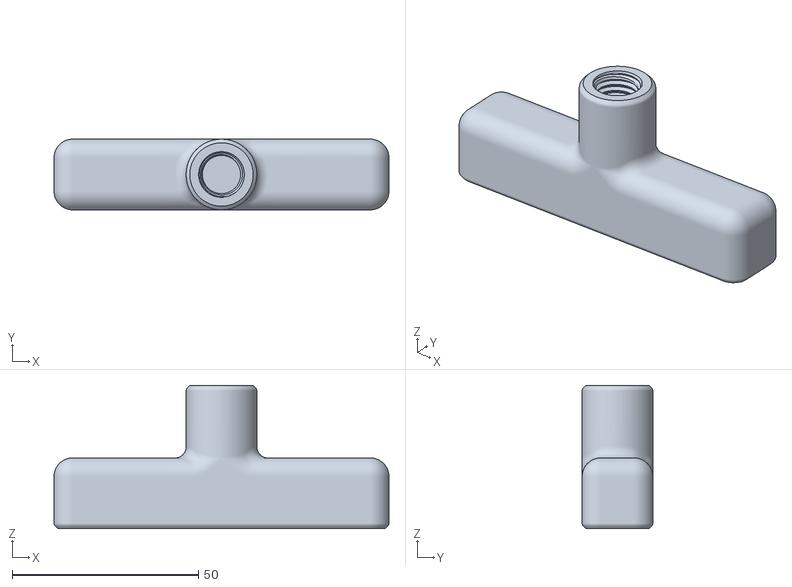
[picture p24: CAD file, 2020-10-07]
Build_Files/3D_Printing/V1.1/OWS_Topper_Tee.stl
90.0 x 19.0 x 38.5

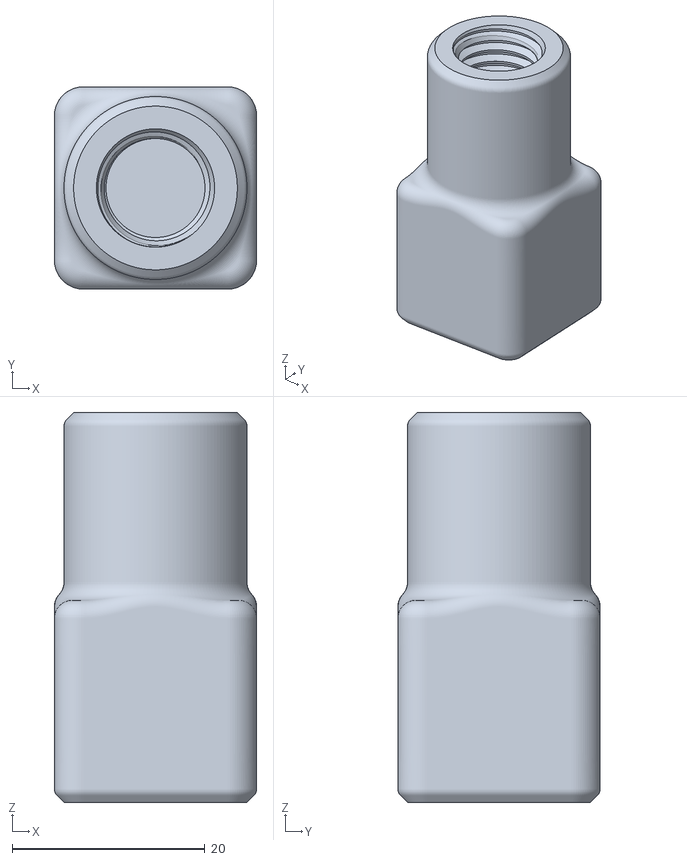
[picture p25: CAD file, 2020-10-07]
Build_Files/3D_Printing/V1.1/OWS_Topper_Square.stl
21.0 x 21.0 x 40.5

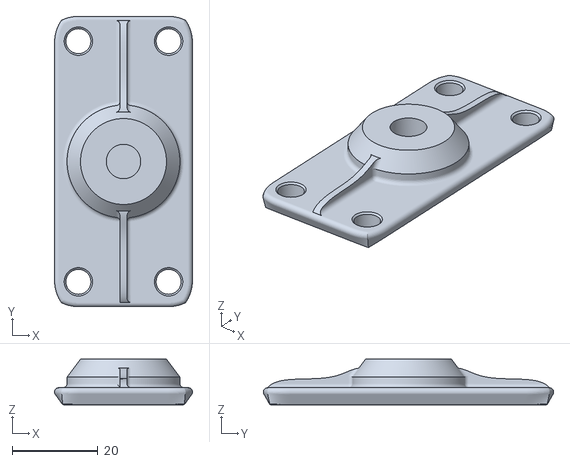
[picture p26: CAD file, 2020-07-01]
Build_Files/3D_Printing/V1.1/OWS_Mounting_Adapter.stl
32.1 x 67.6 x 10.7

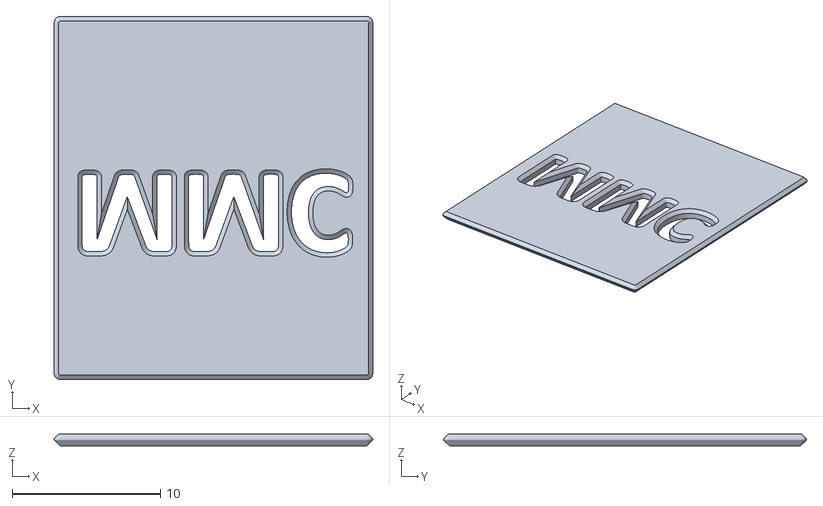
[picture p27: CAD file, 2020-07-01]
Build_Files/3D_Printing/V1.1/OWS_Nameplate.stl
21.5 x 24.5 x 0.8

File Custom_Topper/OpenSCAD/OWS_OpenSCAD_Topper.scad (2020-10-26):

/*
    simplest Open Wobble Switch topper example in OpenSCAD:
        a small sphere on top of a hexagonal base
        
    scruss, 2020-07 - for Makers Making Change - CC-BY-SA
    updated 2020-10
    
    see main project at:
https://www.makersmakingchange.com/project/open-wobble-switch/

This is not intended to be a particularly useful topper, but merely
an example designed with open-source tools to interface with the 
thread on the Open Wobble Switch.

This example creates a small sphere, 22 mm in diameter,
on top of the threaded part. You may change the module topper()
to suit your application.

*/

// from https://dkprojects.net/openscad-threads/
include <threads.scad>;

// please don't change these numbers
thread_diameter     = 12;
thread_pitch        =  1.75;
thread_length       =  7.7 + thread_pitch;
thread_extra        =  0.8;
hex_flats           = 16.5;
hex_corner_radius   =  2;
hex_diameter        = hex_flats / (sqrt(3) / 2);
hex_height          = 16;
hole_diameter       =  2.5;
hole_height         = hex_height + 2;

// ****************
// this is the bit you can change:
// your module should be centred on the origin, or at least
// be centred in X and Y and go below the Z origin somewhat.
module topper() {
    sphere(d=22);
}
// ****************

// please don't change anything after this
difference() {
    // outer envelope
    union() {
        // hexagonal prism with rounded corners
        //   to match OWS_Topper_Base
        linear_extrude(height=hex_height)rotate(90)offset(r=hex_corner_radius)circle(d=hex_diameter - 2 * hex_corner_radius, $fn=6);
        // (example) spherical topper
        translate([0, 0, hex_height])topper();
    }
    // negative space
    union() {
        // thread on switch body
        metric_thread(diameter=thread_diameter + thread_extra,
                        pitch=thread_pitch,
                        length=thread_length,
                        internal=true,
                        leadin=0);
        // rest of switch wire
        cylinder(h=hole_height,
                    d=hole_diameter / (sqrt(3) / 2),
                    $fn=6);
    }
}

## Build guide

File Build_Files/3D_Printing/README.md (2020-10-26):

# Open-Wobble-Switch

<<<<<<< HEAD
## 3D Printing Instructions

### Print Settings
These print settings are for all files:
- Material: PLA
- Nozzle: 0.4 mm
- Infill: 20%
- Support: No
- Resolution: 0.2 mm
- Perimeters: 2

### Files
A single Open Wobble Switch will requires the follwing:
- 1X [OWS_Set.stl](OWS_Set.stl)

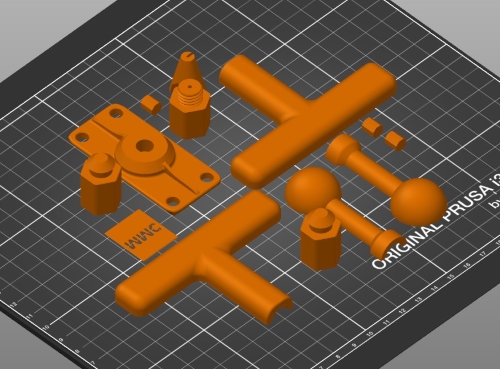
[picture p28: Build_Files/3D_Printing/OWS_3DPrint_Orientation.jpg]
Screenshot of print orientation


Individual files are stored in the [v1.0](/v1.0) folder if you want to print them separately (e.g. different colors, spare parts).

OWS_Set.stl consists of the following files:
 - 1X OWS_Mounting_Adapter.stl
 - 1X OWS_Nameplate.stl
 - 1X OWS_Topper_Gluing_Jig.stl
 - 1X OWS_Topper_Base.stl
 - 1X OWS_Topper_Ball_Set.stl
 - 1X OWS_Topper_Tee_Set.stl

OWS_Topper_Ball_Set.stl consists of the following files:
 - 1X OWS_Topper_Socket.stl
 - 1X OWS_Topper_Pin.stl
 - 1X OWS_Topper_Ball_Top.stl
 - 1X OWS_Topper_Ball_Bottom.stl

OWS_Topper_Tee_Set.stl consists of the following files:
 - 1X OWS_Topper_Socket.stl
 - 2X OWS_Topper_Pin.stl
 - 1X OWS_Topper_Tee_Top.stl
 - 1X OWS_Topper_Tee_Bottom.stl
=======
The necessary files for V1.1 can be found in OWS_All_v1.1.3mf. The individual stl files are available in the versioned folder.

## 3D Printing Settings
Material: PLA
Nozzle: 0.4 mm
Infill: 20%
Support: No
Resolution: 0.2 mm
Perimeters: 2
>>>>>>> Dev

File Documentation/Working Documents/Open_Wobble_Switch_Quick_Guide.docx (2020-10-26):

Introduction

The Open Wobble Switch is a force-activated assistive switch that is activated by moving a wand in any direction. It can be activated using several different body parts including the hand, temple, chin, and tongue (through cheek).

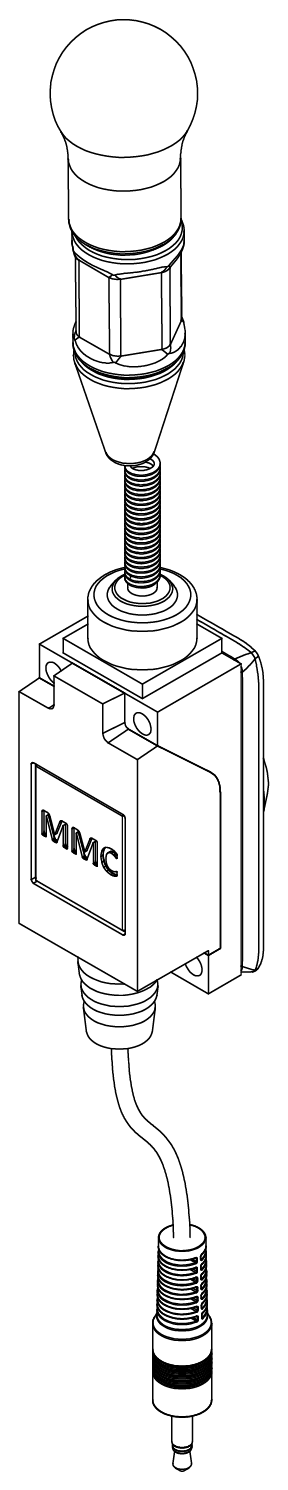
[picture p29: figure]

Features

Topper Top

Topper Base

Switch Body

Mounting Adapter

Mono Cable

Specification

Size | L: 240 mm x W: 30 mm x T: 35 mm
Activation Force | ~0.55 N (55 gf)
Cleaning | Damp Cloth
Disinfection | Ethyl Alcohol, Isopropyl Alcohol, Hydrogen Peroxide

Mounting the Switch

The Wobble Switch has a mounting adapter with a female ¼”- 20 UNC thread, so it can be attached to a variety of camera and other assistive mounting solutions.

Connecting the Switch

1. Connect the 3.5 mm cable from the switch to the assistive device.

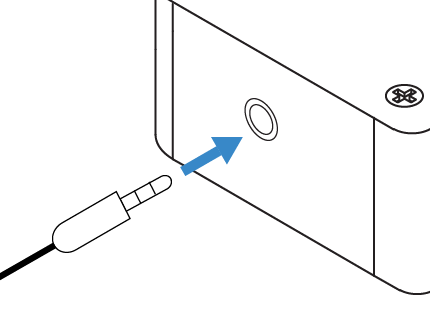
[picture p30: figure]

# Activating the Switch

1. Activate the switch by applying force onto the wand.

# Swapping Topper Tops

1. Remove the existing Topper Top by holding the Topper Top and Topper Base and unscrewing the threads.
2. Attach the new Topper Top by holding the Topper Base and screwing in the threads.

© 2020 by Neil Squire. “Open Wobble Switch Quick Guide” licensed under the CC BY SA 4.0 License: http://creativecommons.org/licenses/by-sa/4.0 PAGE 1 OF 1 Design files available at https://www.makersmakingchange.com/project/open-wobble-switch/

V1.1 | OCTOBER 2020 Open Wobble Switch Quick GUIDE

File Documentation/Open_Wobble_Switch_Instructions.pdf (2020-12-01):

01. Remove the cover by unscrewing the 3 screws. | 02. Cut the mono cable in half to a 6’ length and put the cable through the flexible strain relief.
0 1 cm 2 cm | TWIST 04. Twist the exposed wire and strip the 2nd wire with the plastic sheath 2 cm.

### 03. Strip 4 cm length of cable with a

wire stripper to expose the two internal wires.

05. Unscrew the top 2 “NO” screws (not “NC”) just enough (1-2 full turns) so the plate is exposed. | 06. Twist the short wire and slide the two wires between the plates.
07. Screw the 2 screws back in to hold the cables in place. | 08. Make a loop with the mono cable.

# Open Wobble Switch

# ASSEMBLY MANUAL

V1.1 | tiny.cc/MMCproj | PAGE 1 OF 4 | ORIGINAL DESIGN BY MAKERS MAKING CHANGE

3-4 cm

### 2 cm

# ASSEMBLY MANUAL

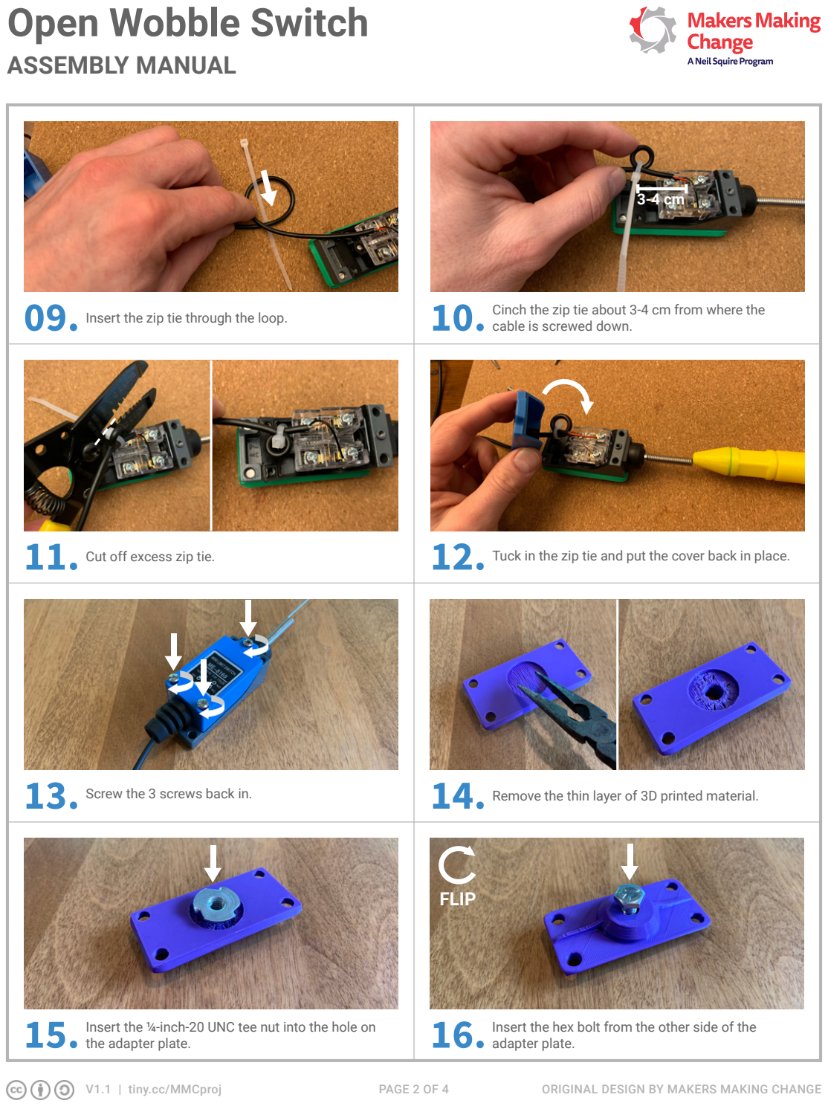
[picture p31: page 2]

V1.1 | tiny.cc/MMCproj | PAGE 2 OF 4 | ORIGINAL DESIGN BY MAKERS MAKING CHANGE
09. Insert the zip tie through the loop. | 10. Cinch the zip tie about 3-4 cm from where the cable is screwed down.
11. Cut off excess zip tie. | | 12. Tuck in the zip tie and put the cover back in place.
13. 14. Screw the 3 screws back in. | Remove the thin layer of 3D printed material.
15. 16. Insert the ¼-inch-20 UNC tee nut into the hole on the adapter plate. | FLIP Insert the hex bolt from the other side of the adapter plate.

3-4 cm

# ASSEMBLY MANUAL

FLIP 17. Using a wrench, screw the hex bolt into the t-nut and tighten until it sits flush. | FLIP 18. Unscrew the bolt.

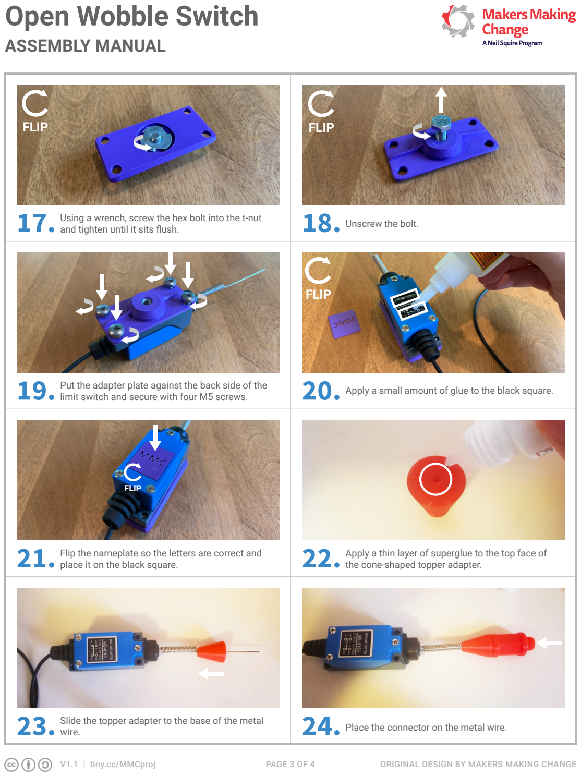
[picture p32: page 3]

V1.1 | tiny.cc/MMCproj | PAGE 3 OF 4 | ORIGINAL DESIGN BY MAKERS MAKING CHANGE
19. Put the adapter plate against the back side of the limit switch and secure with four M5 screws. | FLIP 20. Apply a small amount of glue to the black square.
FLIP 21. 22. Flip the nameplate so the letters are correct and place it on the black square. | Apply a thin layer of superglue to the top face of the cone-shaped topper adapter.
23. 24. Slide the topper adapter to the base of the metal wire. | Place the connector on the metal wire.

# ASSEMBLY MANUAL

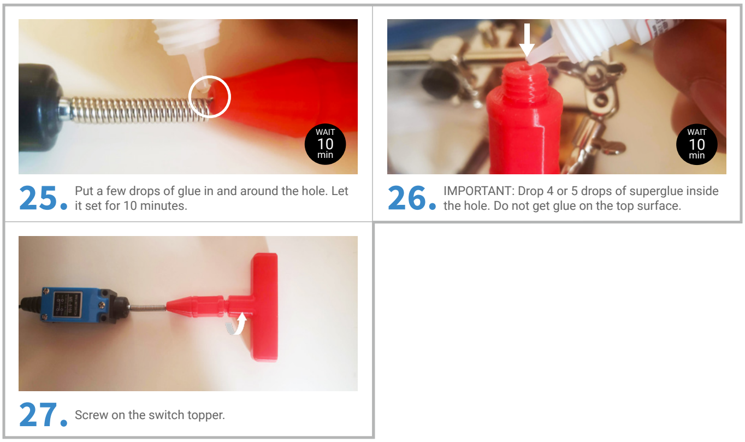
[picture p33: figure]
WAIT 10 min; it set for 10 minutes.; Screw on the switch topper.

V1.1 | tiny.cc/MMCproj | PAGE 4 OF 4 | ORIGINAL DESIGN BY MAKERS MAKING CHANGE

### 26. IMPORTANT: Drop 4 or 5 drops of superglue inside

the hole. Do not get glue on the top surface.

Put a few drops of glue in and around the hole. Let

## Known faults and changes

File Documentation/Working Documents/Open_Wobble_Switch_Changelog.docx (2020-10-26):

V1.1

- Created transition piece
- Redesigned wand topper adapter
- Redesigned Tee topper
  - Reduced length and weight to improve actuation
  - One-piece design
- Redesigned Ball topper
  - Reduced length and weight to improve actuation

V1.0

- Replaced wand topper with modular two-part threaded component
  - Added T-topper
  - Added Hand-shaped topper

V0.1

- Initial proof of concept featuring 4-part wand topper with captive rings.

© 2020 by Neil Squire. “Open Wobble Switch Changelog” is licensed under the CC BY SA 4.0 License: http://creativecommons.org/licenses/by-sa/4.0 PAGE 1 OF 3 Design files available at https://www.makersmakingchange.com/project/open-wobble-switch/

V1.1 | OCTOBER 2020 Open Wobble Switch Changelog

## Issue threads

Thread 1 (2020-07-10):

### ISSUE TITLE
Upper Ring very difficult to remove from bed

### ISSUE THREAD

**Issue by scruss** [makersmakingchange/Open-Wobble-Switch#1]
`OWS_Wand_Ring_Upper_v0.1.stl` is thin, flexible and curves inwards. Consequently it's very hard to remove from the print bed. The typical tools couldn't shift it: had to resort to putting the Prusa print bed in the freezer.

A small outward chamfer to allow a tool underneath to lever the part off would be appreciated.

**Comment by jakemcivor** [comment]
OWS_Wand_Ring_Upper_v0.1.stl was removed in v1.0

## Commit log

2020-04-22 Prototype Upload
    Initial prototype for ME8169 style limit switch. 4 part friction fit ball wand topper.
    [OWS_Mounting_Adapter_v0.1.stl, OWS_Nameplate_v0.1.stl, OWS_Set_v0.1.stl, OWS_Wand_Ball_v0.1.stl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]
2020-07-01 Pre-publish commit
    [Limit Switch ME 8169 v9.f3z, OWS_Mounting_Adapter.stl, OWS_Mounting_Adapter_v0.1.stl, OWS_Nameplate.stl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]
2020-07-01 Clean-up
    This reverts commit eb0cf89f2c41626ffaee44081b0beca365508f07.
    [Limit Switch ME 8169 v9.f3z, OWS_Mounting_Adapter.stl, OWS_Mounting_Adapter_v0.1.stl, OWS_Nameplate.stl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]
2020-07-01 Revert "Clean-up"
    This reverts commit 949c4d92cf05233a7c5cfd86d67a6bb6fe0c790e.
    [Limit Switch ME 8169 v9.f3z, OWS_Mounting_Adapter.stl, OWS_Mounting_Adapter_v0.1.stl, OWS_Nameplate.stl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]
2020-07-01 Remove unused docs
    [Open_Wobble_Switch_BOM.xlsx]
2020-07-06 Add BOM and update Readme
    [Open_Wobble_Switch_BOM.xlsx]
2020-07-06 Add 3d models for Custom Toppers
    [Wobble_Topper_Flat.stl, Wobble_Topper_Flat_Combined.stl, Wobble_Topper_Flat_Thread.stl]
2020-07-09 Separate custom toppers files
    [OWS_OpenSCAD_Topper.scad, Wobble_Topper_Flat.stl, Wobble_Topper_Flat_Combined.stl, Wobble_Topper_Flat_Thread.stl]
2020-07-10 Print file simplification
    Separate individual print files and clarify instructions.
    [OWS_Mounting_Adapter.stl, OWS_Nameplate.stl, OWS_Topper_Ball_Bottom.stl, OWS_Topper_Ball_Top.stl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]
2020-07-10 Update README.md
    Clarify 3d Printing instructions
2020-07-10 Clean 3D print files
    Update links in readme.
    Correct set as switch + tee + ball
    [OWS_Topper_Ball_Set.stl, OWS_Topper_Hand_Set..stl, OWS_Topper_Tee_Set.stl]
2020-10-13 Update README.md
    Correct assembly link
2020-10-26 V1.1 Print file update
    [OWS_All_v1.1.3mf, OWS_Mounting_Adapter.stl, OWS_Mounting_Adapter_v0.1.stl, OWS_Nameplate.stl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]
2020-10-26 Update custom topper for v1.1
    [OWS_OpenSCAD_Topper.scad, Open_Wobble_Topper-ShortBall.stl, Wobble_Topper_Flat.stl, Wobble_Topper_Flat_Combined.stl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]
2020-10-26 v1.1 design file cleanup
    [Limit Switch ME 8169 v9.f3z, Wobble Ball Topper v5.f3z, Wobble_Mounting_Adapter v10.f3d, Wobble_Nameplate v4.f3d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]
2020-10-26 v1.1 documentation cleanup
    [Open_Wobble_Switch_BOM.xlsx, Open_Wobble_Switch_BOM_v1.1.xlsx]
2020-10-26 v1.1 Cleanup
    [OSW_All_Topper_Pieces.3mf, OSW_Ball_Topper.3mf, OSW_Peg_Topper.3mf, OSW_Peg_Topper.stl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]
2024-03-21 Update documentation filenames
    Remove version from filenames; update readme
    [Open_Wobble_Switch_BOM.xlsx, Open_Wobble_Switch_BOM_v1.1.xlsx]
2024-03-21 Add csv version of BOM
    Easier access for GitHub
    [Open_Wobble_Switch_BOM.csv, Open_Wobble_Switch_BOM.xlsx]
2026-01-05 Update BOM 3D print links to 'main' branch
    Changed all GitHub URLs in the BOM from 'master' to 'main' to reflect repository branch updates. Updated both CSV and XLSX BOM files for consistency.
